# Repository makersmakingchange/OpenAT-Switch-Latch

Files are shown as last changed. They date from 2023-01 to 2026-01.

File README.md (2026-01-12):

<!--- Open Source Assistive Technology: GitHub Readme Template Version 1.2 (2024-May-27)  --->

<!--- TITLE --->
# OpenAT Switch Latch 
The OpenAT Switch Latch is a switch adapter that enables a standard momentary assistive switch to be used as a toggle switch or latch. Activating and releasing the input switch will turn on and hold on the output. Activating and releasing the input switch again will turn the connected output device off. The device requires one CR2032 coin cell battery for operation. 

This device was developed as several assistive switch users requested the ability to control lights and other devices in a semi-permanent manner utilizing their preferred momentary assistive switches.

The OpenAT Switch Latch is comprised of off-the-shelf electronics, a custom printed circuit board (PCB) and 3D printed parts.

The OpenAT Switch Latch is open assistive technology (OpenAT). Under the terms of the open source licenses, the device may be built, used, and improved upon by anyone.

The overall cost of materials for a single build is approximately $67 CAD. The cost of materials when built in quantity is $38 CAD.

> [!IMPORTANT]
2025-Nov-06: One of the electronic components in this design has been discontinued (MOSFET IRLD014PBF) and is no longer available on DigiKey or Mouser. In the short term, there are some alternative sources (e.g., https://www.amazon.ca/10PCS-IRLD110-DIP4-IRLD110PBF-DIP-4/dp/B0DSSJTPH8). In the longer term, we are working on updating the design with an alternative component.  

Last updated: 2026-Jan-12

## Usage
To setup the OpenAT Switch Latch, a momentary switch is plugged into the 3.5 mm jack marked 'Input' and the device to be controlled is plugged into the 3.5 mm jack marked 'Output'.

To use the device it must be powered on by sliding the Power Switch towards the left to the On position. When the assistive switch is activated, the LED indicator light will turn on and remain on, and the output device will be activated. When the assistive switch is activated again, the LED indicitor light will turn off and remain off, and the output device will be deactivated.

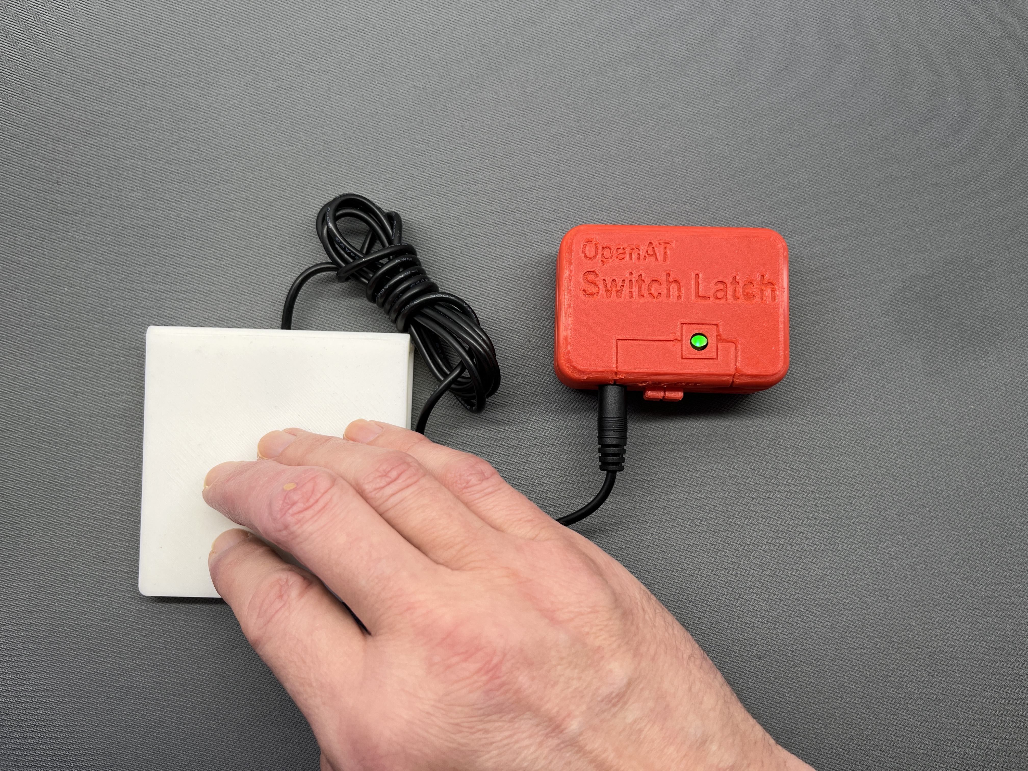
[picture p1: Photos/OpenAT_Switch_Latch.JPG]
An OpenAT Switch Latch pictured with a person pressing an input switch.


## More info at
- [Makers Making Change Library Page](https://www.makersmakingchange.com/s/product/switch-latch/01tJR00000095zlYAA)

## How to Obtain a OpenAT-Switch-Latch
### 1. Do it Yourself (DIY) or Do it Together (DIT)

This is an open-source assistive technology, so anyone is free to build it. All of the files and instructions required to build the OpenAT-Switch-Latch are contained within this repository. Refer to the Maker Checklist below.

### 2. Request a build of this device

If you would like to obtain a OpenAT Switch Latch, you may submit a build request through the [MMC Library Page](https://www.makersmakingchange.com/s/product/switch-latch/01tJR00000095zlYAA). The requestor is responsible for the cost of materials and any shipping.

### 3. How to build this device for someone else

If you have the skills and equipment to build this device, and would like to donate your time to create the switch for someone who needs it, visit the [MMC Maker Wanted](https://makersmakingchange.com/maker-wanted/) section.

## Getting Started

### 1. Read the Makers Checklist

The [Makers Checklist](/Documentation/OpenAT_Switch_Latch_Maker_Checklist.pdf) provides an overview of the steps required to build this device.

### 2. Order the Off-The-Shelf Components

The [Bill of Materials](/Documentation/OpenAT_Switch_Latch_BOM.csv) lists all of the parts and components required to build the OpenAT-Switch-Latch. The main switch component needs to be ordered online. The rest of the off-the-shelf components are also online or may be available in smaller quantities at your local hardware store or dollar store.

### 3. Order the PCBs

The [Gerber_Files](/Build_Files/PCB_Build_Files/Gerber_Files) includes the PCB build information which can be submitted to PCB fabrication service to create the custom PCB. Please refer to MMC-PCB for more information on custom PCB fabrication.

### 4. Print the 3D Printable components

All of the files and individual print files can be in the [/Build_Files/3D_Printing_Files](/Build_Files/3D_Printing_Files/) folder.

### 5. Assemble the OpenAT-Switch-Latch

Reference the [Assembly Guide](/Documentation/OpenAT_Switch_Latch_Assembly_Guide.pdf) for the tools and steps required to build each portion.

## Files

### Documentation
| Document             | Version | Link |
|----------------------|---------|------|
| Design Rationale     | 1.0     | [OpenAT_Switch_Latch_Design_Rationale](/Documentation/OpenAT_Switch_Latch_Design_Rationale.pdf)     |
| Maker Checklist      | 1.0     | [OpenAT_Switch_Latch_Maker_Checklist](/Documentation/OpenAT_Switch_Latch_Maker_Checklist.pdf)     |
| Bill of Materials    | 1.2.1    | [OpenAT_Switch_Latch_Bill_of_Materials](/Documentation/OpenAT_Switch_Latch_BOM.csv)     |
| 3D Printing Guide    | 1.0     | [OpenAT_Switch_Latch_3D_Printing_Guide](/Documentation/OpenAT_Switch_Latch_3D_Printing_Guide.pdf)     |
| Assembly Guide       | 1.2.1     | [OpenAT_Switch_Latch_Assembly_Guide](/Documentation/OpenAT_Switch_Latch_Assembly_Guide.pdf)     |
| User Guide           | 1.0     | [OpenAT_Switch_Latch_User_Guide](/Documentation/OpenAT_Switch_Latch_User_Guide.pdf)    |

### Design Files

 - [CAD Design Files](/Design_Files/CAD_Design_Files)
 - [PCB Design Files](/Design_Files/PCB_Design_Files)

### Build Files

 - [3D Printing Files](/Build_Files/3D_Printing_Files)
 - [PCB Build Files](/Build_Files/PCB_Build_Files)

## License
Copyright (c) 2023-2024 Neil Squire Society.

This repository describes Open Hardware:
 - Everything needed or used to design, make, test, or prepare the OpenAT Switch Latch is licensed under the [CERN 2.0 Weakly Reciprocal license (CERN-OHL-W v2) or later](https://cern.ch/cern-ohl ) .
  - Accompanying material such as instruction manuals, videos, and other copyrightable works that are useful but not necessary to design, make, test, or prepare the Forest Hub are published under a [Creative Commons Attribution-ShareAlike 4.0 license (CC BY-SA 4.0)](https://creativecommons.org/licenses/by-sa/4.0/) .

You may redistribute and modify this documentation and make products using it under the terms of the [CERN-OHL-W v2](https://cern.ch/cern-ohl).
This documentation is distributed WITHOUT ANY EXPRESS OR IMPLIED WARRANTY, INCLUDING OF MERCHANTABILITY, SATISFACTORY QUALITY AND FITNESS FOR A PARTICULAR PURPOSE.
Please see the CERN-OHL-W v2 for applicable conditions.

Source Location: https://github.com/makersmakingchange/OpenAT-Switch-Latch

## Contributors
 
 - Derrick Andrews, Neil Squire Society. Concept generation, circuit design, testing, documentation.
 - Milad Hajihassan, Neil Squire Society. PCB Layout.
 - Jake Mclvor, Neil Squire Society. Enclosure design, documentation. 

---

<!-- ABOUT MMC START -->
## About Makers Making Change
[Makers Making Change Logo](https://www.makersmakingchange.com/)

Makers Making Change is a program of [Neil Squire](https://www.neilsquire.ca/), a Canadian non-profit that uses technology, knowledge, and passion to empower people with disabilities.

Makers Making Change leverages the capacity of community based Makers, Disability Professionals and Volunteers to develop and deliver affordable Open Source Assistive Technologies.

 - Website: [www.MakersMakingChange.com](https://www.makersmakingchange.com/)
 - GitHub: [makersmakingchange](https://github.com/makersmakingchange)
 - Bluesky: [@makersmakingchange.bsky.social](https://bsky.app/profile/makersmakingchange.bsky.social)
 - Instagram: [@makersmakingchange](https://www.instagram.com/makersmakingchange)
 - Facebook: [makersmakechange](https://www.facebook.com/makersmakechange)
 - LinkedIn: [Neil Squire Society](https://www.linkedin.com/company/neil-squire-society/)
 - Thingiverse: [makersmakingchange](https://www.thingiverse.com/makersmakingchange/about)
 - Printables: [MakersMakingChange](https://www.printables.com/@MakersMakingChange)

### Contact Us
For technical questions, to get involved, or to share your experience we encourage you to [visit our website](https://www.makersmakingchange.com/) or [contact us](https://www.makersmakingchange.com/s/contact).
<!-- ABOUT MMC END -->

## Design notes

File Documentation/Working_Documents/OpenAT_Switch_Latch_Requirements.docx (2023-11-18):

### 1.1.1 Introduction

Many assistive switches are the momentary type; however, it is often desirable to use such switches in a toggle switch manner to allow long duration use of a switched device.

# 1. Problem Definition

## 1.1 Who

Who will be using the device?

- Users who are unable (or prefer not) to activate an assistive switch for extended time periods.

Who will be affected by the device?

- Users who wish to control lights and other devices in a semi permanent manner, by utilizing their preferred momentary assistive switches.

## 1.2 What

What must the device do?

- Set a toggle switch output to it’s opposite state, whenever the assistive switch is connected to the input, and enabled.

What needs must the device serve?

- Ability to control lights, tools, music effects, or toys for long durations.

## 1.3 Why

Why will the device be used?

- Because existing assistive switches are usually momentary, and toggleable switches are unlikely to be found in many assistive switch classes.

## 1.4 Where

- In homes, offices, or other work environments.

## 1.5 When

- When a device needs to be enabled for more than a few seconds.

# 2. Functional Properties

## 2.1 Goals

ID | Description
G01 | Cost-effective
G02 | Optimized for low-volume builds (I.e., 1)
G03 | Open-Source Hardware
G04 | Enable a momentary assistive switch to toggle (latch) a switch controllable device.
G05 | Minimize material cost
G06 | Sustainability

## 2.2 Functional Requirements

ID | Description
F01 | The device shall have one or more input channels.
F02 | Long duration operation (many days of operation on battery power).
F03 | The device should have a visual feedback element to indicate switch activation ( Example: LED)
F04 | The device should allow activation by plugging a cable into the input jack and should default to a non-closed connection.
F05 | The OpenAT Switch Latch should have a power switch to reduce power consumption when not being used.
F06 | The battery hatch should provide a screw to prevent children from swallowing the lid or the battery underneath.
F07 | The device should have a capacitor for input circuit switch input debouncing, as the device will not be able to achieve this using software.
F08 | When off, the circuit must activate (and stay active) when a switch input is triggered.
F09 | When on, the circuit must de-activate (and stay off) when a switch input is triggered.
F10 | The circuit must contain some form of switch debouncing circuitry to keep operation reliable.

## 2.3 Non-functional Requirement

ID | Description
NF01 | Shall look professional with tight tolerance on case size.
NF02 | Input ports should be legibly labelled for easy identification
NF03 | The device should require no mechanical force to operate.
NF04 | The device should have a long battery life.
NF05 | The toggle Adapter should use a minimum of electronic parts.

## 2.4 Constraints

ID | Description
C01 | The OpenAT Switch Latch must be able to be constructed using basic ‘maker’ tools.
C02 | The OpenAT Switch Latch should be able to be disinfected using detergent and alcohol.

© 2023 by Neil Squire / Makers Making Change. This work is licensed under the CC BY SA 4.0 License: http://creativecommons.org/licenses/by-sa/4.0 Files available at https://makersmakingchange.com/project/OpenAT-Switch-Latch/ Page 1 of 1

V1.0 | January 2023 OpenAT-Switch-Latch requirements Specifications

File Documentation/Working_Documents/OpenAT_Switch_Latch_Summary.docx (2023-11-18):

# Title

## OpenAT Switch Latch

## Subtitle

A switch adapter that allows a momentary assistive switch to act as a toggle switch.

## Device Specifications

Build Time:

< 1hr

Cost:

$50-$100

Stage: Recently Added

Skills:

Need: Electronics, Soldering, 3D Printing, Custom PCB, Engineering

Disability: Mobility / Physical, Cognitive / Learning

Difficulty: Intermediate

License: Attribution-ShareAlike 4.0 International

Usages: Aids for Daily Living, Environmental Control, Recreation and Leisure, Computer Access

Type:

Designer: Makers Making Change

## Device Details

### Overview

### The OpenAT Switch Latch converts a momentary switch input into a toggle switch output. The device was developed as several assistive switch users requested the ability to control lights and other devices in a semi-permanent manner, but do so, utilizing their preferred momentary assistive switches.

### The intended users of the OpenAT Switch Latch are those who require a momentary switch to act as a toggle switch (e.g., latched switch), allowing the user to turn on for an extended time with a quick tap, and off again with another quick tap.

### Usage

### To setup the Open AT Switch Latch adapter, a momentary switch is plugged into the 3.5 mm jack marked 'Input' and the device to be controlled is plugged into the 3.5 mm jack marked 'Output'.

To use the device it must be powered on by sliding the Power Switch towards the left to the On position. When the assistive switch is activated, the LED indicator light will turn on and remain on, and the output device will be activated. When the assistive switch is activated again, the LED indicator light will turn off and remain off, and the output device will be deactivated.

### Cost

~$50.54 ($20.54 Components and 3D prints; ~$30 for 5 custom PCBs)

### Build Instructions

The OpenAT Switch Latch consists of 3D printed parts, a custom PCB, and electronic components. All documentation including an Assembly Guide is available at the GitHub repository.

#### Skills Required

- 3D Printing
- Soldering
- Custom PCB

#### Time Required

- 3D Printing Time: 2 Hours and 40 Minutes
- Assembly Time: 1 Hour

#### Tools

- Soldering Iron and 60/40 electronics solder
- Needle nose pliers
- Side cutters
- Medium Phillips screwdriver

#### Components

1. 1X 470K Resistor
2. 1X 22K Resistor
3. 1X Texas Instruments CD74HC73E Flip-Flop
4. 1X 1uF Capacitor
5. 1X #4-3/6" Pan Head Screw
6. 1X OpenAT-Switch-Latch PCB (Printed Circuit Board)
7. 1X CR2032 Battery holder
8. 2X IRLD-110 MOSFET
9. 1X 10K Resistor
10. 1X 0.1uF Capacitor
11. 2X SJ-3566AN 3.5mm Audio Stereo Jack
12. 1X Slide Switch
13. 1X LED (green, super bright)
14. 4X #4-3/8" Pan Head Screw
15. 1 X CR2032 Battery

#### 3D Printing

1. 1X 3D Printed Enclosure Top
2. 1X 3D Printed Enclosure Bottom
3. 1X 3D Printed LED Spacer
4. 1X 3D Printed Switch Slide
5. 1X 3D Printed Battery Cover

#### Custom PCB

This design utilizes a custom PCB. Five boards (minimum quantity) can be obtained for approximately $30 CAD (shipping included).

### Design

The PCB was designed using Autodesk EAGLE, and the enclosure was designed using Autodesk Fusion 360.

### Attribution

Designed by Makers Making Change

- Circuit design by Derrick Andrews, Makers Making Change
- PCB Layout by Milad Hajihassan, Makers Making Change
- Enclosure design by Jake Mclvor, Makers Making Change

© 2023 by Neil Squire / Makers Making Change. This work is licensed under the CC BY SA 4.0 License: http://creativecommons.org/licenses/by-sa/4.0 Files available at https://makersmakingchange.com/project/OpenAT-Switch-Latch/ Page 1 of 2

V1.0 | December 2022 OpenAT Switch Latch Summary

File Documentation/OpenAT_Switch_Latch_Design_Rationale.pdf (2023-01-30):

V1.0 | Aug 2022

## OpenAT Switch Latch

## DESIGN RATIONALE

© 2023 by Neil Squire / Makers Making Change. This work is licensed under the CC BY SA 4.0 License: http://creativecommons.org/licenses/by-sa/4.0 Files available at https://makersmakingchange.com/project/OpenAT-Switch-Latch/

### Introduction

The OpenAT Switch Latch was developed when a number of assistive switch users (Ean Price, Tom Cretain) requested the ability to control lights and other devices in a semi permanent manner, but do so, utilizing their preferred momentary assistive switches.

The intended users of the OpenAT Switch Latch are those who require a momentary switch to act as a toggle switch (aka latched switch), allowing the user to turn on for an extended time with a quick tap, and off again with another quick tap.

### Research

### Commercial Options

AbleNet Dual Switch Latch & Timer

The Dual Switch Latch & Timer by Adaptive Tech Solution $305.22

Switch Latch & Timer (adaptivetechsolutions.com) (https://www.adaptivetechsolutions.com/dual-switch-latch-timer/)

Most switches give switch users momentary control of their switch adapted toys or appliances. Meaning, when you press your switch, your toy or appliance will operate only for the time that you are holding down the switch. The Dual Switch Latch and Timer gives switch users more control of their devices by adding time and latch modes of control. You can setup two switches into the Switch Latch and timer. The switches will operate their corresponding toy or appliance independently of each other in the same mode of control.

Switch Capable Continuous Control Unit

## DESIGN RATIONALE

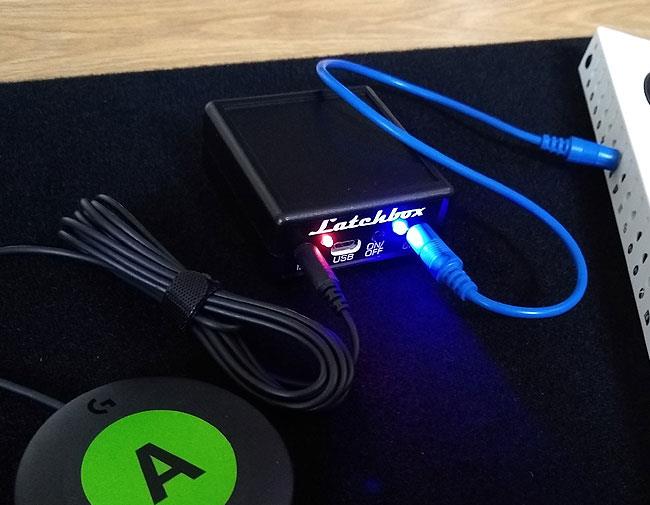
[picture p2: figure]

© 2023 by Neil Squire / Makers Making Change.

can be used to operate most AC appliances from up to 20 feet away. List Price: $315.40 Sale
Price: $220.56 (Save 30%)

The Switch Capable Continuous Control Unit can be used to operate most AC appliances from up to 20 feet away. Activate the remote transmitter with a capability switch after plugging the appliance into the receiver. In latch mode, the appliance will run until the switch is pressed again; in momentary mode, it will turn on when the switch is pressed and off as soon as the switch is released.

PowerLink 4
https://www.ablenetinc.com/powerlink-4-north-america/

Cost: $330 USD + Shipping

Used to turn on appliances that are powered from a wall outlet.

Latch Box
Link: https://oneswitch.org.uk/art.php?id=276

Cost: £40 (+ postage) (~$62 CAD + shipping)

Power: 3x AAA batteries OR USB (Micro-B)

## DESIGN RATIONALE

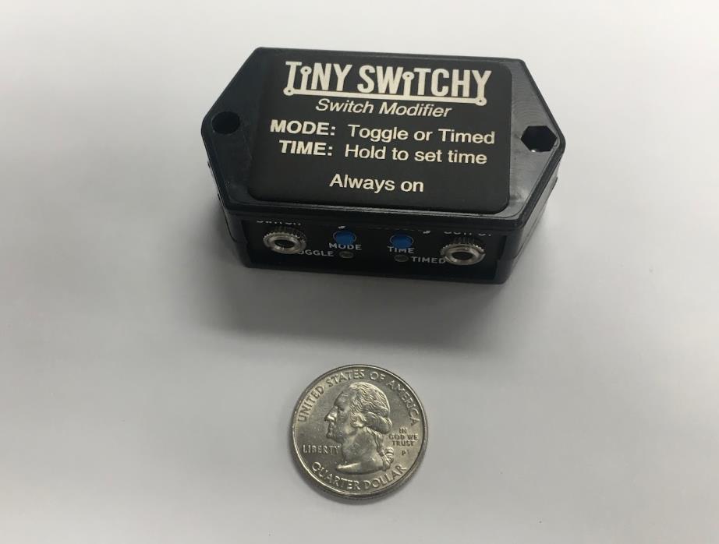
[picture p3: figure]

© 2023 by Neil Squire / Makers Making Change.

Tiny Switchy Version 1.4

Information: https://www.tinyswitchy.com/

Purchase: https://www.littlelaketech.com/product/tiny-switchy/1#

Cost: $40 USD + Shipping. Does not currently ship to Canada.

- Toggle and timed-output modes
- 3V CR2032 Coin cell battery
- Expected battery life: 3 years
- Small
- >1 A switched current
- Maximum hold time: 68 minutes

### DIY Versions

Self-Retention for Button on Xbox Adaptive Controller
Link: http://www.johannes-online.de/wordpress/?page_id=1063
- Based on request from Melly (https://meilert.net/) (https://twitter.com/melly_maeh)
- LED to indicate status

## DESIGN RATIONALE

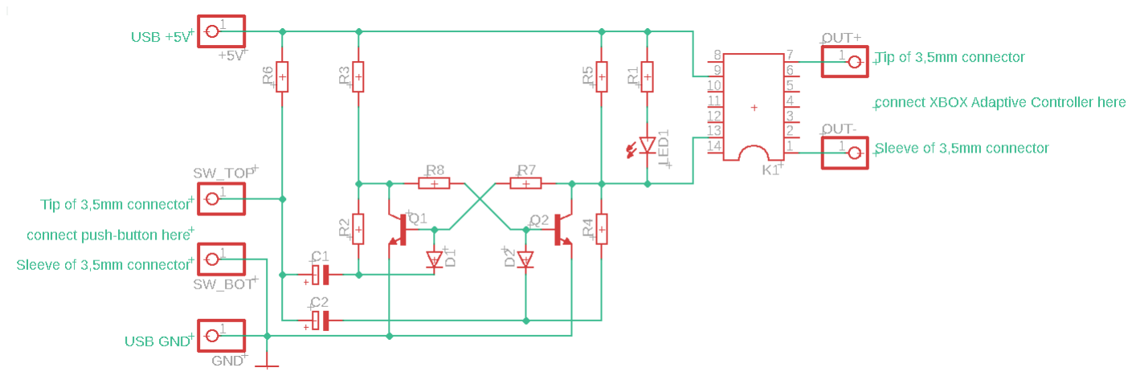
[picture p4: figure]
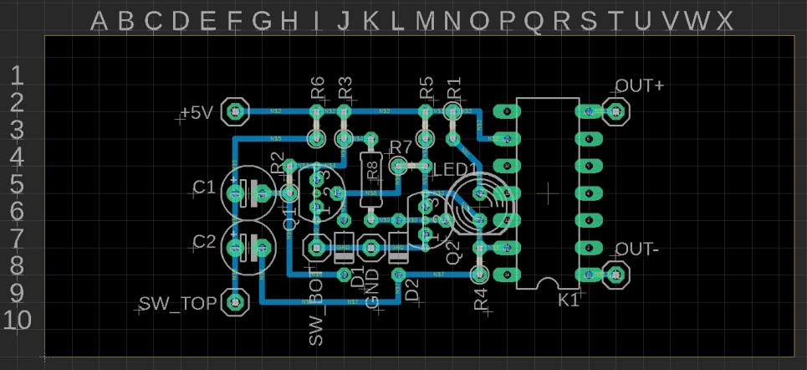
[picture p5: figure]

© 2023 by Neil Squire / Makers Making Change.

Position | Designation | Number
C1, C2 | Electrolytic capacitor 22 μF | 2
D1, D2 | Diode 1N4007 | 2
K1 | Reed Relay V23100-V4005-A010 | 1
LED1 | LED 5mm, red | 1
Q1, Q2 | Transistor BC547 | 2
R1, R2, R3, R4, R5 | Resistor 1k Ohm | 5
R6, R7, R8 | Resistance 10k Ohm | 3

30 mm x 70 mm Grid board

## DESIGN RATIONALE

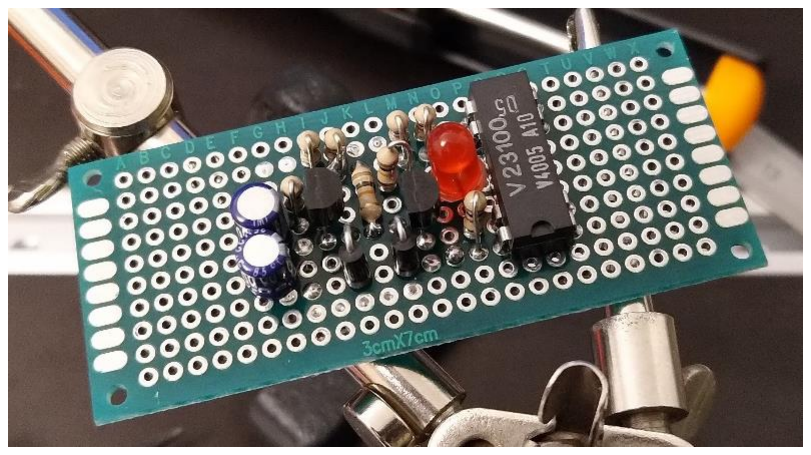
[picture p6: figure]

© 2023 by Neil Squire / Makers Making Change.

https://youtu.be/RP3qliKeLuE

https://youtu.be/2iWaojsw_O0

### Requirements

### Goals

G01 | Enable a momentary assistive switch to toggle (latch) a switch controllable device.
G02 | To make the device with a relay output capable of driving powered devices.
G03 | To make the unit accept 3.5 mm assistive switches.
G04 | Battery life of XX

### Functional Requirements

F01 | When off, the toggle circuit must activate (and stay active) when a switch input is triggered.
F02 | When on, the toggle circuit must de-activate (and stay off) when a switch input is triggered.
F03 | The toggle circuit must contain some form of switch debouncing circuitry to keep operation reliable.
F04 | The toggle circuit should default to a non-closed connection.

### Non-functional Requirement

NF01 | The Toggle Adapter should require no mechanical force to operate.
NF02 | The toggle Adapter should have a long battery life.

## DESIGN RATIONALE

© 2023 by Neil Squire / Makers Making Change.

NF03 The toggle Adapter should use a minimum of electronic parts.

### Constraints

C01 | The MMC Toggle Adapter must be able to be constructed using basic ‘maker’ tools.
C02 | The MMC Toggle Adapter should be able to be disinfected using detergent and alcohol.

## DESIGN RATIONALE

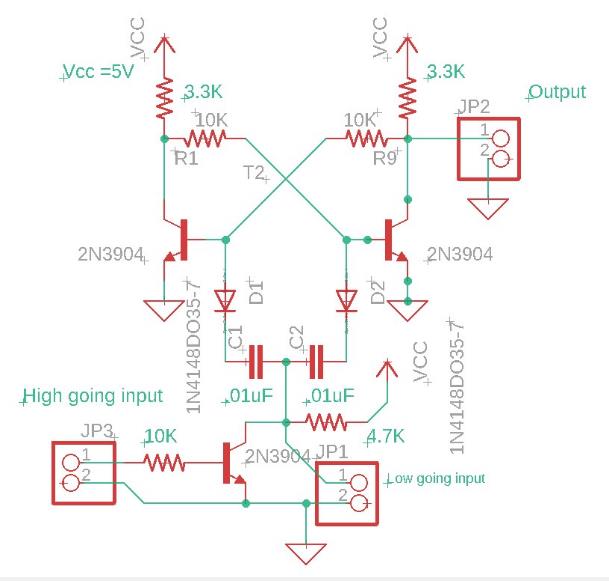
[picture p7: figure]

© 2023 by Neil Squire / Makers Making Change.

### Ideation

Some electronic toggle circuit diagrams were sourced from the internet as potential candidates for forming the core of the MMC Toggle Adapter. The ideal candidate circuit will have inexpensive parts that are small in number and are easy to construct with basic hand tools.

### Conceptual Design

### Toggle Circuit Options

Concept 1: Two Transistor Flip-Flop

Two Transistor Flip Flop circuit

This circuit comprises of just two low cost and extremely available transistor and a reasonable number of resistors and capacitors. As no microchip is required, many electronics engineers and hobbyists will find they already posses the needed garden variety parts. The main downsides are that more parts are needed, and that the power consumption of this concept is highest.

## DESIGN RATIONALE

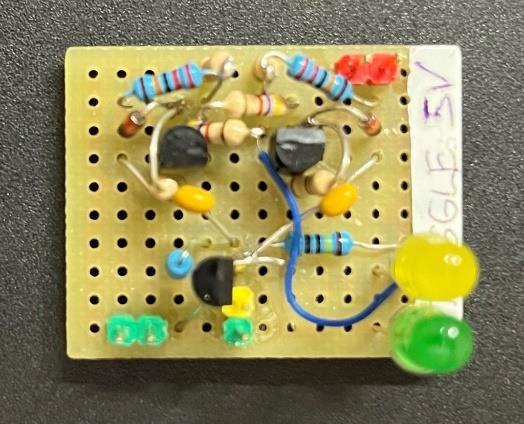
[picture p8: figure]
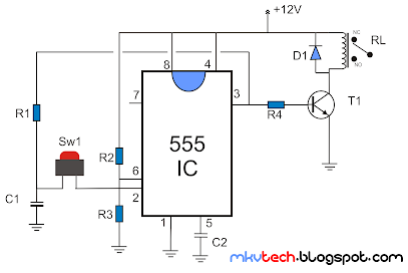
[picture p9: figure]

© 2023 by Neil Squire / Makers Making Change.

Concept 1 prototype was built on Perfboard using parts already in stock. As the parts count is quite high having a PCB design would be best for the final version The diode steering works reliably, as the discrete bipolar transistors have a higher noise immunity than CMOS type input circuitry. The downside comes in the form of higher power consumption, which can be a problem if using batteries.

Concept 2: 555 Timer IC

555 Timer IC

The venerable 555 Timer IC is used for the second concept. Note that the lower power CMOS version is used here. The chip is easy to solder as it only has eight pins. Power consumption is about 80 micro amps, the second lowest.

## DESIGN RATIONALE

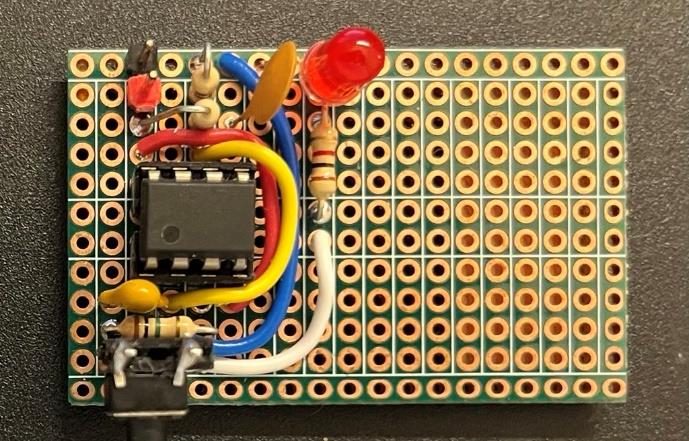
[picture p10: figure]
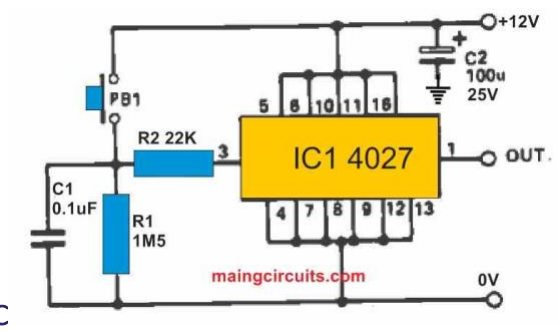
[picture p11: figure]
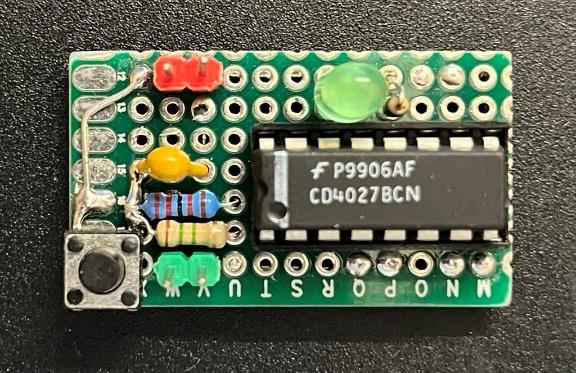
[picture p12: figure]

© 2023 by Neil Squire / Makers Making Change.

The concept 2 prototype was built on double sided Perfboard using parts ordered from Digi-Key. Note that this circuit makes use of the CMOS version of the 555 timer IC, which is considerably more energy efficient than the original (but still available) bipolar version. Putting this one together was noticeably easier, as the total part count is nearly half that of the discrete transistor version.

Concept 3: Dual Flip Flop IC
The low power CMOS CD4027BCN Dual Flip Flop IC is used here. While the IC has 16 pins to solder, they can all be soldered quickly because all pins go into a PCB together, and can be soldered quickly due to being placed in rows. Note that this chip has the lowest power consumption of the concepts presented here. Current draw is a mere .7 micro amps, so this circuit could run on a coin cell for months.

Concept 3 prototype was built on double sided Perfboard using parts ordered from Digi-Key. The low power CMOS CD4027BCN Dual Flip Flop IC is used here. While the IC has 16 pins to solder, they can all

## DESIGN RATIONALE

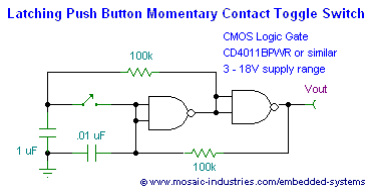
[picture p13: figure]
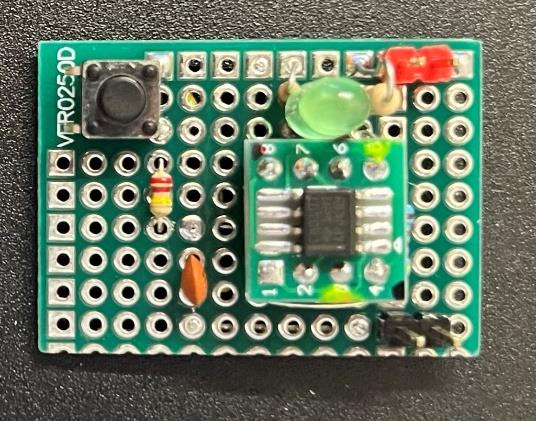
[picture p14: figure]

© 2023 by Neil Squire / Makers Making Change.

be soldered quickly as they are in rows, and all go in together. Note that this chip has the lowest power consumption of the concepts presented here. Current draw is a mere .7 micro amps, so this circuit could run on a coin cell for months. An additional bonus of this design is that this IC can be used to make two toggle switches without having to buy another chip. It just requires an extra three resistors, and a capacitor of the same values.

Concept 4: Quad NAND Gate IC CD40107BM96 dual NAND gate

Concept 3 prototype was built on double sided Perfboard using parts ordered from Digi-Key. The low power CMOS CD4027BCN Dual Flip Flop IC is used here. ng, so the design was changed to incorporate a bearing instead.

## DESIGN RATIONALE

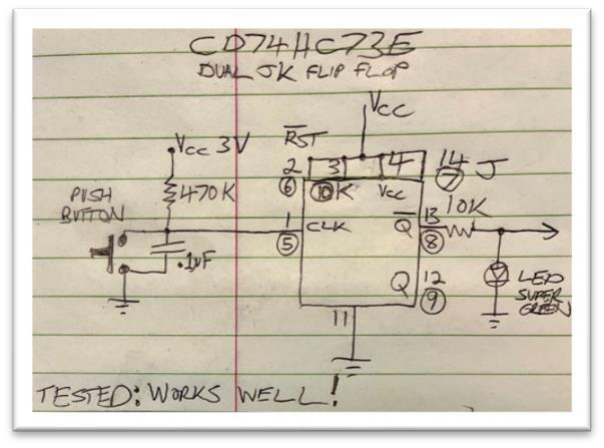
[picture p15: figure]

© 2023 by Neil Squire / Makers Making Change.

Concept 5 Flip Flop with buffered inputs
The CD74HC73E was chosen when it was determined that the input circuitry of the flip flop was vital to the behaviour of the latching circuit when fed with a mechanical switch instead of normally expected CMOS or TTL level circuitry. It was found, that despite identical part numbers, parts from different manufacturers had different input structures suitable for switch inputs. We liked the CD74HC73E because it had an input buffer that could condition a rougher input signal into a usable form, without having to add extra circuitry. Additionally, this chip drew remarkably little power, while still being able to provide decent output drive.

Component List:

### Circuit Comparison

| Concept 1 Discrete transistor Flip-Flop | Concept 2 555 Timer IC | Concept 3 CD4027 Flip-Flop IC | Concept 4 Quad NAND gate IC | Concept 5 TI CD74HC73E Dual Flip Flop
Current Draw (all at 3.3V) | 959 uA (2.37 mA + LED) | 88-90 uA (1.35+LED) | .2 uA (86.2 uA+LED) | 4.9 uA | .4uA 67uA with LED on
Noise Immunity | Excellent | Poor: pin 2 input of 555 highly susceptible to | Acceptable: .85 VAC RMS | Fail Circuit fails to change states when | Excellent

## DESIGN RATIONALE

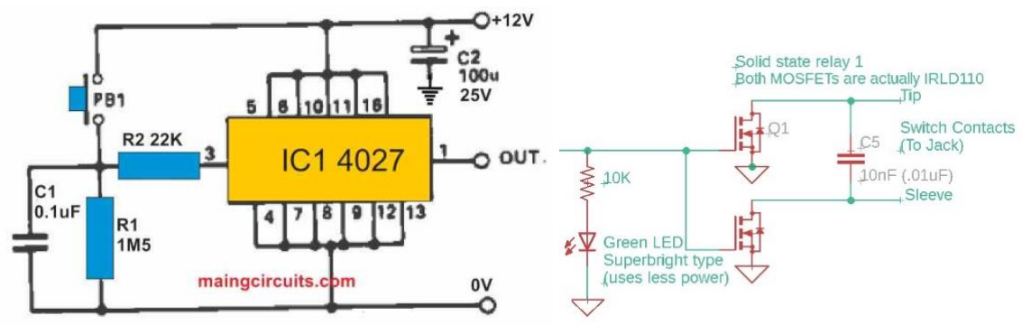
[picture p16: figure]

© 2023 by Neil Squire / Makers Making Change.

| withstood 1.7 VAC RMS) on input | noise .25 VAC RMS | | wires are added. | Works even with longer cables
Price | Under $20 for core circuitry | Under $20 for core circuitry | Under $20 for core circuitry | Under $20 for core circuitry | Under $20 for core circuitry
Projected ease of build | Moderate | Very Easy | Easy | Easy | Easy

### Toggle Circuit

As the leading design from the comparison table is using the CD4027 IC, we will focus on the CD4027. Note that all the test circuits omitted a solid state relay output circuit, which we will add to the final design, and will become sum of the two schematics below:

## DESIGN RATIONALE

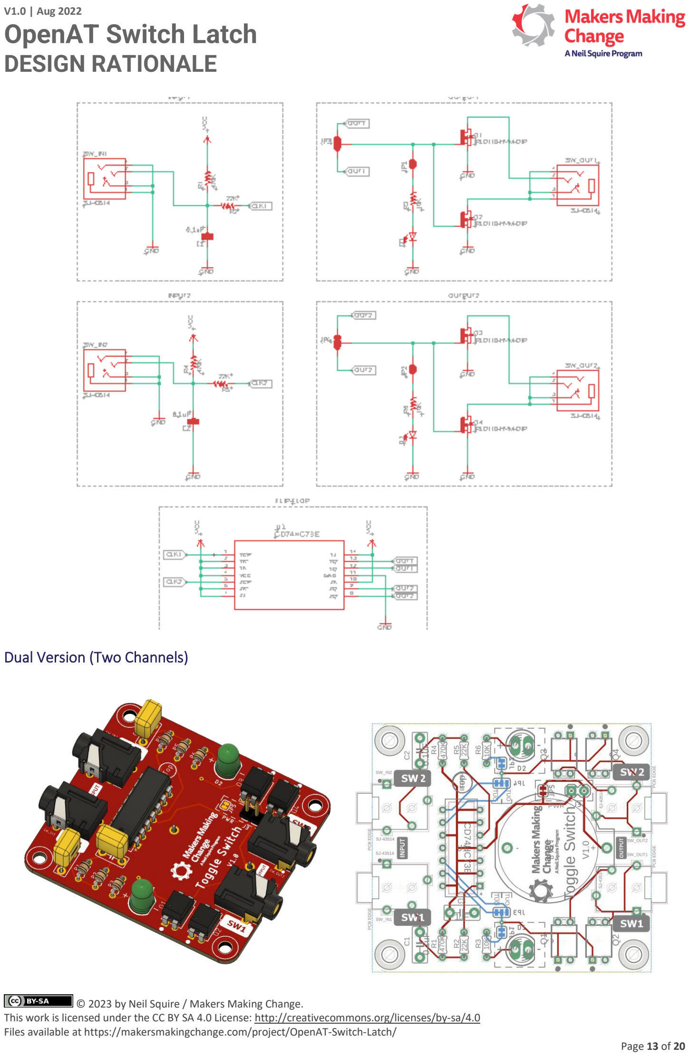
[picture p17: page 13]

© 2023 by Neil Squire / Makers Making Change.

Dual Version (Two Channels)

## DESIGN RATIONALE

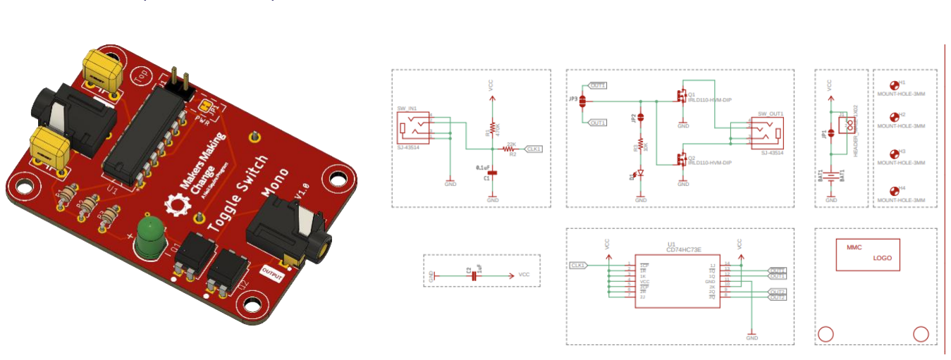
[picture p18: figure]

© 2023 by Neil Squire / Makers Making Change.

Dual Construction Method Comparison
| PCB | PCB-A Thru-hole | PCB-A SMD | Protoboard
Number of components | 22 | N/A | N/A | N/A
Number of polarized components | 7 | N/A | N/A | N/A
Number of connections | 72 | N/A | N/A | N/A
Cost | $28 CAD | N/A | N/A | N/A
Size | 56mm x 50mm | N/A | N/A | N/A
Maker Difficulty | Medium | Medium | High | High

Mono Version 1 (One Channel)

## DESIGN RATIONALE

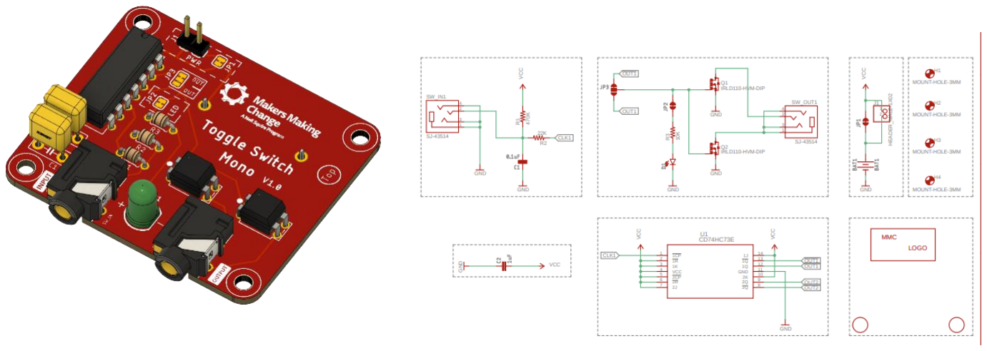
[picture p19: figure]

© 2023 by Neil Squire / Makers Making Change.

Mono Version 2 (One Channel)

Mono Construction Method Comparison
| PCB | PCB-A Thru-hole | PCB-A SMD | Protoboard
Number of components | 12 | N/A | N/A | N/A
Number of polarized components | 4 | N/A | N/A | N/A
Number of connections | 46 | N/A | N/A | Additional jumpers needed on protoboards
Cost | $20 CAD | N/A | N/A | N/A
Size | 56mm x 38mm or 52mm x 44mm | N/A | N/A | Additional area may be needed
Maker Difficulty | Easy | Moderate | SMD soldering skills needed | Recommend Experienced builders only

## DESIGN RATIONALE

© 2023 by Neil Squire / Makers Making Change.

### Power Source

AAA Cells
Pros
- Rechargeable

Cons

- Can leak over long time durations

Lithum 3V Cells
Pros
- High energy density, unlikely to leak.

Cons

- Potential fire risk for some brands/formulations

Comparison

AAA cells are more readily available in stores, but 3V lithium batteries are less common, though CR2032 coin cells are reasonably common.

### Layout

### Visual Feedback

(Nothing)

LED
High brightness (efficient) green LED used with higher value resistor for lower current draw.

### Test Button

No test button is chosen.

### Power Switch

Internal jack switch

## DESIGN RATIONALE

© 2023 by Neil Squire / Makers Making Change.

External slide switch

### Detailed Design

### OpenAT Switch Latch V1.0

Channels
This design uses a single channel.

Visual Feedback
This design has a single green LED. When the output is closed, the LED is on. When the output is open, the LED is off. There is a cuttable junction for disabling this feature.

Power Source
3V Lithium CR2032 Cell in a thru-hole mounted holder.

Power Switch
This design has a sliding power switch.

Enclosure
This design has a multipart 3D printed enclosure fastened with screws. The enclosure consists of a top, bottom, battery cover, and switch slide. The PCB is affixed inside to the top portion of the enclosure. The bottom of the enclosure is affixed to the top of the enclosure using four (4) screws. The battery cover is held in with a single screw.

## DESIGN RATIONALE

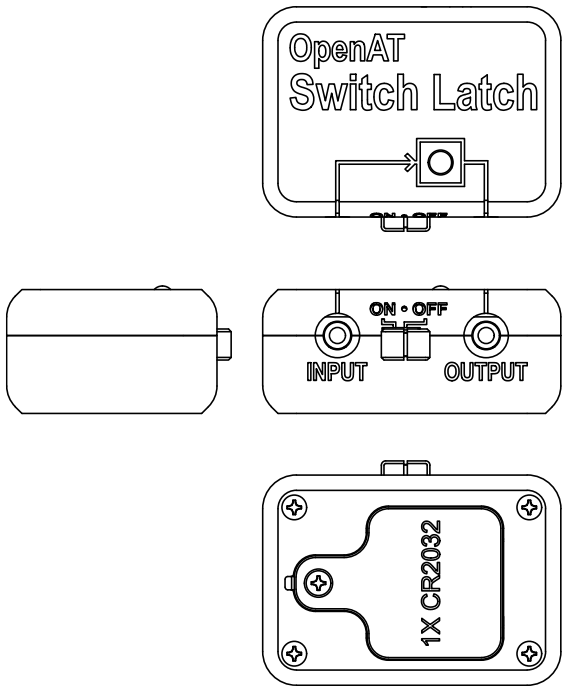
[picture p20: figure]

© 2023 by Neil Squire / Makers Making Change.

Layout

Design Changes
- Add footprint for right angle switch with a cut-able bypass junction (switch on by default)
- Add Jack with built in switch to act power switch and mark switch pins on PCB (to allow for bypass in case of failure I.e. Digi-Key SJ-3566AN or equivalent)
- Add Clearance around the PCB and battery holder (2.5-3 mm?)
- Add central hole on PCB same size as 4 corner holes.
- Change Dimensions of PCB to 60 x 40 mm
- Move alternate output cut-able trace to under battery case (allows for testing but not final use)
- Move input and output jacks apart as much as possible (but allow 1mm clearance to case posts)
- Move the power switch between input and output jacks
- Move LED to right of switch
- Change the JK flip flop IC to Texas Instruments CD74HC73E, as CD4027 from Fairchild was no longer available from Digi-Key or Mouser, and the newer revisions from other vendors had gate

## DESIGN RATIONALE

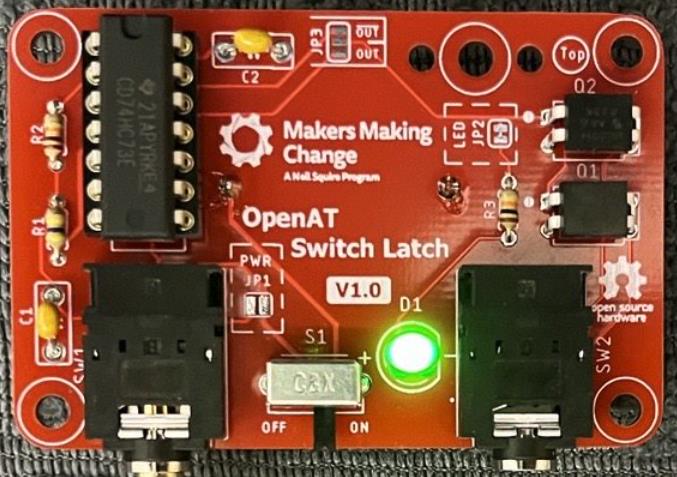
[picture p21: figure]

© 2023 by Neil Squire / Makers Making Change.

input structures that proved unsuitable for use with a mechanical switch input, as this type of circuit is normally fed with pulses from another logic IC

### Opportunities for Improvement

- Modify design with extra capacitor (or diode) to boost the noise immunity somewhat.
- Use non polarized ceramic capacitor for power decoupling.
- Modify circuit to become a dual toggle switch, as only six extra parts are required.
•

Printed Circuit Board

Theory of Operation

- Pressing the button causes the input of the first JK Flip Flop to go low. This triggers the Flip Flop output to change to its opposite state, and remaining that way (even after the button is released, and the input goes high again). Only a fresh button press will change the output state. The output of the Flip Flop feeds a green LED for state indication, via a 10K resistor. The Flip Flop output is also connected to two MOSFETs, which are wired together to function as a solid state relay. Thus, when the Flip Flop output goes high, and the LED turns on, the output jack also becomes conductive, turning on any connected and activatable device.

## DESIGN RATIONALE

© 2023 by Neil Squire / Makers Making Change.

JP1

- Default: Unsoldered
- Purpose: This can be soldered to bypass the input jack switch (i.e., the device’s power is controlled only by the power switch)

JP2

- Default: Soldered
- Purpose: This can be cut to disable the Output LED.

JP3

- Default: Reverse toggle switch operation

Final PCB Changes

- Change name
- Move JP3 to be accessible when device is constructed.

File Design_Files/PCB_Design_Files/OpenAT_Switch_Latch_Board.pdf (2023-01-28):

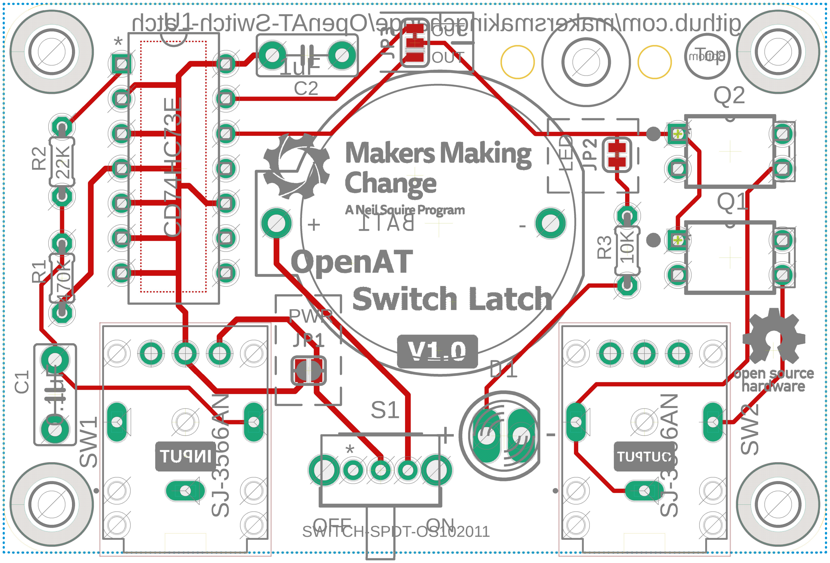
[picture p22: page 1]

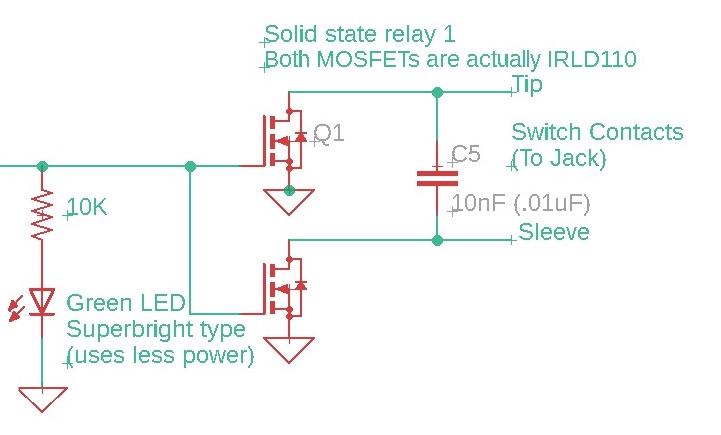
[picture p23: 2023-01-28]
Documentation/Working_Documents/Photos/Solid State relay schematic.jpg

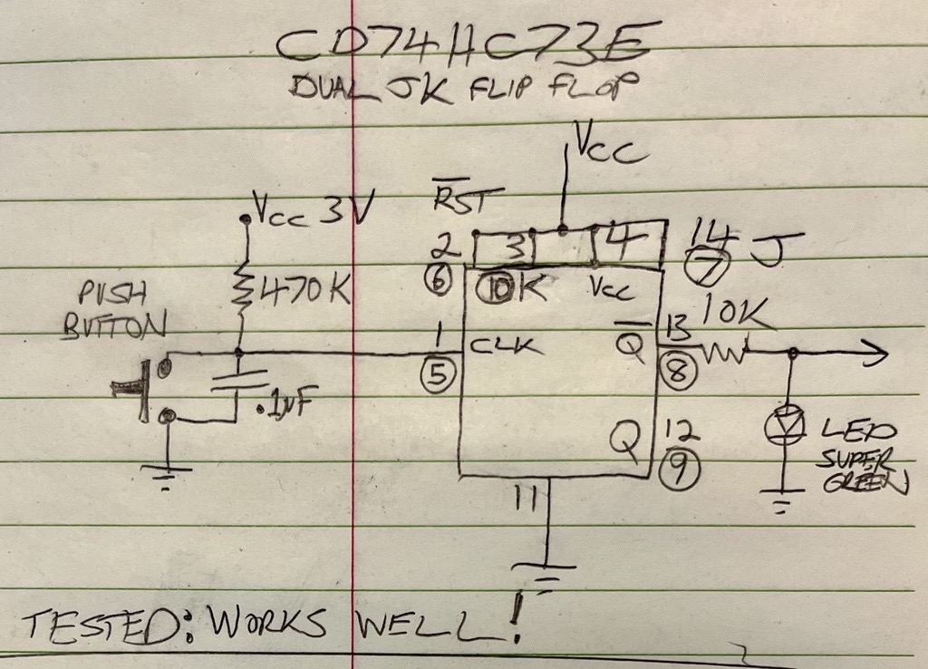
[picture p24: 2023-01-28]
Documentation/Working_Documents/Photos/Switch_Latch_SchematicSketch.png

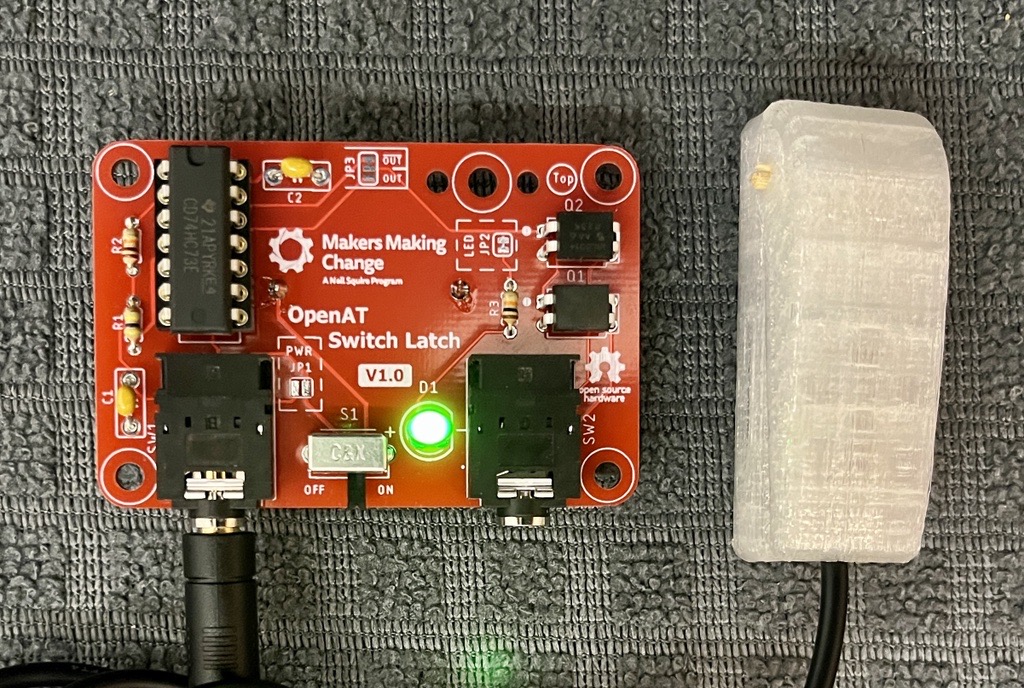
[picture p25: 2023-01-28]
Documentation/Working_Documents/Photos/OpenAtSwitchLatchV1pt0_populatedPCB.png

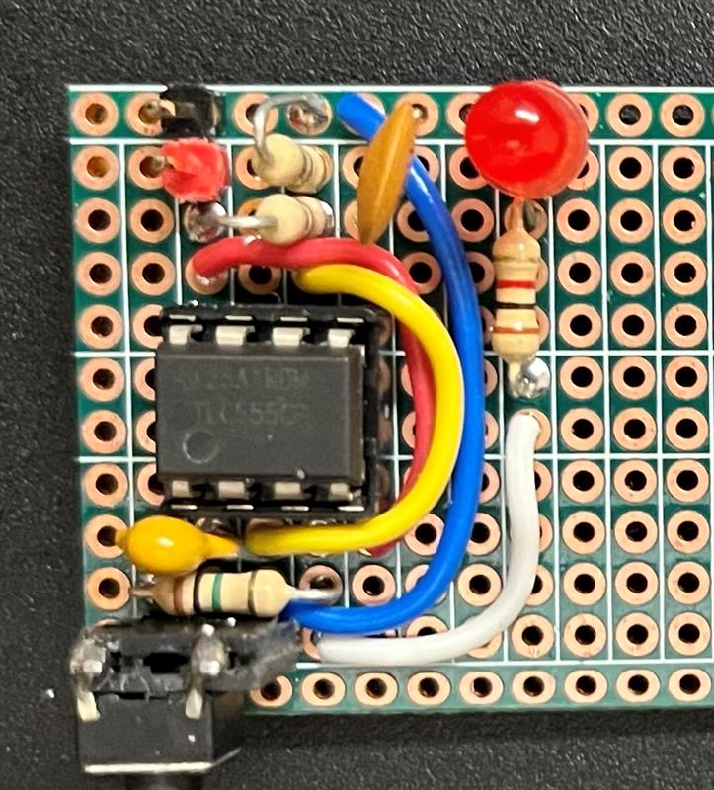
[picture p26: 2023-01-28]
Documentation/Working_Documents/Photos/555_toggle.jpg

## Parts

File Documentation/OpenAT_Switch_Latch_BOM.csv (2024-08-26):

OpenAT Switch Latch
Version: | V1.2.1
Last Updated: | 2024-Aug-26
 |  |  |  |  |  |  |  | Total filament (g) |  | Unit Cost | Total Estimated Cost | Build Cost
 |  |  |  |  |  |  |  | 27.3 |  | $36.91 | $62.86
ID | Commercial Parts |  |  |  |  |  |  |  |  | $30.41 | $33.16
 | Part | Description |  | Manufacturer | Supplier | QTY / Device | QTY / PKG | PKGs | $/ PKG | $ / Device | Total Estimated Cost |  | Link
10 | U1 | CD74HC73E JK Flip Flop |  |  |  | 1 | 1 | 1 | $0.94 | $0.94 | $0.94 |  | https://www.digikey.ca/en/products/detail/texas-instruments/CD74HC73E/1507453
9 | Q1,Q2 | IRLD014PBF 60V 1.2A MOSFET |  |  |  | 2 | 1 | 2 | $2.25 | $4.50 | $4.50 |  | https://www.digikey.ca/en/products/detail/vishay-siliconix/IRLD014PBF/812481
8 | SW1,SW2 | SJ-3566AN 3.5mm Jack Stereo |  |  |  | 2 | 1 | 2 | $2.80 | $5.60 | $5.60 |  | https://www.digikey.ca/en/products/detail/cui-devices/SJ-3566AN/305112
2 | R1 | 470 kOhms 1/8W Through Hole Resistor |  |  |  | 1 | 1 | 1 | $0.15 | $0.15 | $0.15 |  | https://www.digikey.ca/en/products/detail/stackpole-electronics-inc/CF18JT470K/1741719
3 | R2 | 22 kOhms 1/8W Through Hole Resistor |  |  |  | 1 | 1 | 1 | $0.15 | $0.15 | $0.15 |  | https://www.digikey.ca/en/products/detail/stackpole-electronics-inc/CF18JT22K0/1741643
4 | R3 | 10 kOhms 1/8W Through Hole Resistor |  |  |  | 1 | 1 | 1 | $0.15 | $0.15 | $0.15 |  | https://www.digikey.ca/en/products/detail/stackpole-electronics-inc/CF18JT10K0/1741566
5 | C1 | 0.1 µF ±10% Capacitor |  |  |  | 1 | 1 | 1 | $0.46 | $0.46 | $0.46 |  | https://www.digikey.ca/en/products/detail/kemet/C315C104M5U5TA/817927
6 | C2 | 1 µF ±10% Capacitor |  |  |  | 1 | 1 | 1 | $1.15 | $1.15 | $1.15 |  | https://www.digikey.ca/en/products/detail/kemet/C315C105K3R5TA/3726118
13 | BAT1 | 20 mm Coin Cell Battery Holder |  |  |  | 1 | 1 | 1 | $1.69 | $1.69 | $1.69 |  | https://www.digikey.ca/en/products/detail/mpd-memory-protection-devices/BS-7/389447
11 | D1 | 5 mm Green LED |  |  |  | 1 | 1 | 1 | $0.46 | $0.46 | $0.46 |  | https://www.digikey.ca/en/products/detail/creeled-inc/C5SMF-GJE-CX14Q7T2/4794039
7 | S1 | Slide Switch |  |  |  | 1 | 1 | 1 | $0.75 | $0.75 | $0.75 |  | https://www.digikey.ca/en/products/detail/c-k/OS102011MA1QS1/1981431
19 |  | #4-3/8" Pan Head Screw |  |  |  | 6 | 1 | 6 | $0.61 | $3.66 | $3.66 |  | https://www.digikey.ca/en/products/detail/serpac/6005/307599
14 |  | Coin Cell Battery, CR2032 |  |  |  | 1 | 2 | 1 | $5.50 | $2.75 | $5.50
 |  | Digikey Shipping |  |  |  | 1 | 1 | 1 | $8.00 | $8.00 | $8.00
 | Custom PCB |  |  |  |  |  |  |  |  | $5.80 | $29.00
 | Part | Description |  | Manufacturer | Supplier | QTY / Device | QTY / PKG | PKGs | $/ PKG | $ / Device | Total Estimated Cost |  | Link
1 | PCB1 | Custom PCB |  |  |  | 1 | 5 | 1 | $4.00 | $0.80 | $4.00
 | Shipping | Economical Global Direct Line |  |  |  | 1 | 5 | 1 | $25.00 | $5.00 | $25.00
 | 3D Printed Parts |  |  |  |  |  |  | 27.3 |  | $0.70 | $0.70
 | Part | Description | Filament Type | Filament | Color | QTY / Device | Mass (g) / Part | Total Mass | $ / kg | $ / Device | Total Estimated Cost |  | Link
15 |  | Enclosure Top | PLA |  | Any | 1 | 11.4 | 11.4 | $25.00 | $0.29 | $0.29
17 |  | Enclosure Bottom | PLA |  | Any | 1 | 11.4 | 11.4 | $26.00 | $0.30 | $0.30
18 |  | Battery Cover | PLA |  | Any | 1 | 3.3 | 3.3 | $27.00 | $0.09 | $0.09
16 |  | Switch Slide | PLA |  | Any | 1 | 0.7 | 0.7 | $28.00 | $0.02 | $0.02
12 |  | LED Spacer | PLA |  | Any | 1 | 0.5 | 0.5 | $29.00 | $0.01 | $0.01
 | Tools
 | Tool | Description |  | Manufacturer | Supplier |  |  |  |  |  |  |  | Link
 | Screwdriver | Medium Phillips
 | Needle nose pliers
 | Side Cutters
 | Soldering Iron
 | Solder | 60/40 rosin core solder for electronics
 | Multimeter
 | Alternatives
 | Part | Description |  | Manufacturer | Supplier | QTY / Device | QTY / PKG | PKGs | $/ PKG | $ / Device | Total Estimated Cost |  | Link

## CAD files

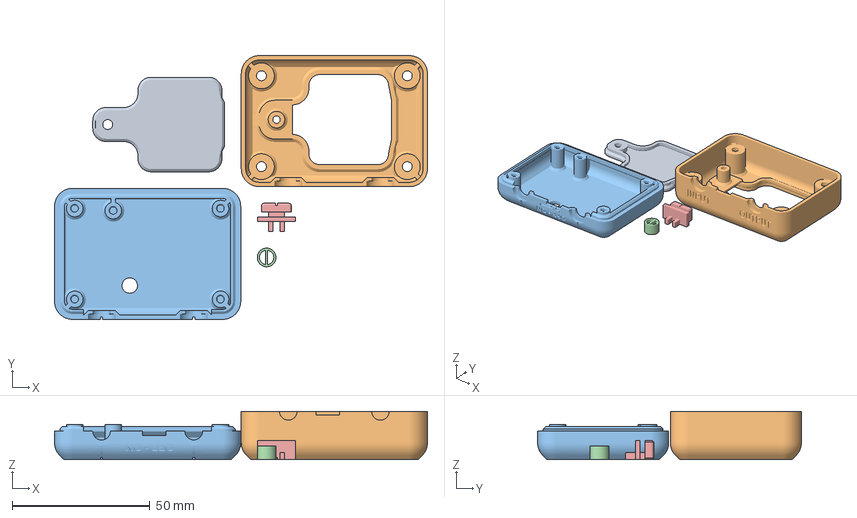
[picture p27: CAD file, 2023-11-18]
Build_Files/3D_Printing_Files/OpenAT_Switch_Latch_v54.3mf
135.6 x 95.9 x 17.6 mm
Battery_Cover.stl
Enclosure_Bottom.stl
Enclosure_Top.stl
LED_Spacer.stl
Switch_Slide.stl

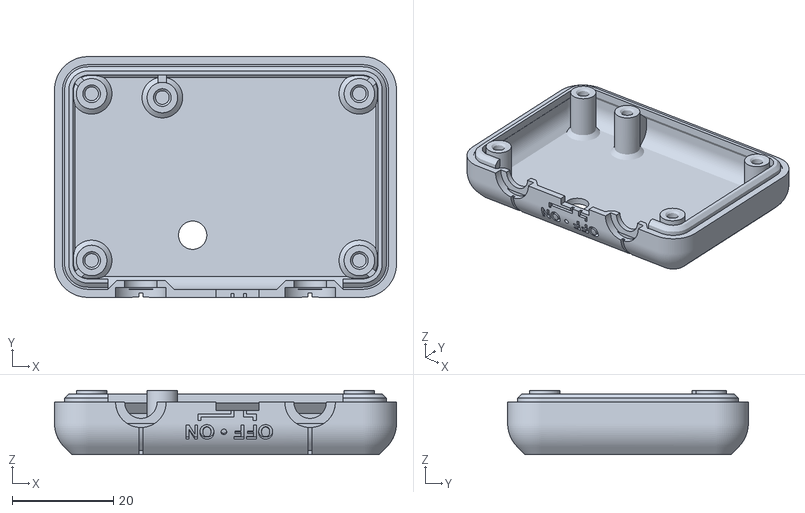
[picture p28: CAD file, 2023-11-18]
Build_Files/3D_Printing_Files/Enclosure_Top.stl
67.7 x 47.6 x 12.7

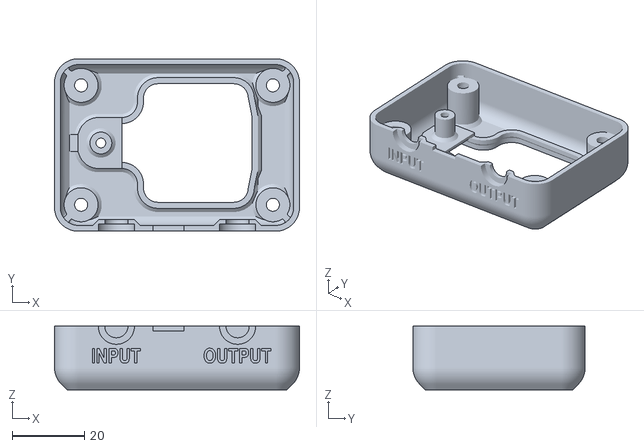
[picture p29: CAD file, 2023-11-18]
Build_Files/3D_Printing_Files/Enclosure_Bottom.stl
67.7 x 47.6 x 17.6

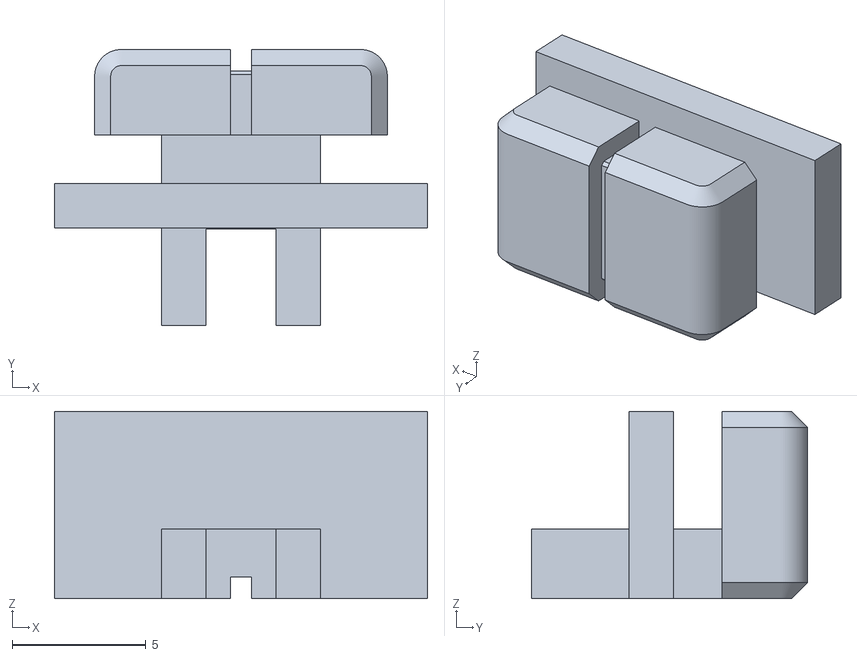
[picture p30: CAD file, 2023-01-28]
Build_Files/3D_Printing_Files/Switch_Slide.stl
13.9 x 10.3 x 7.00

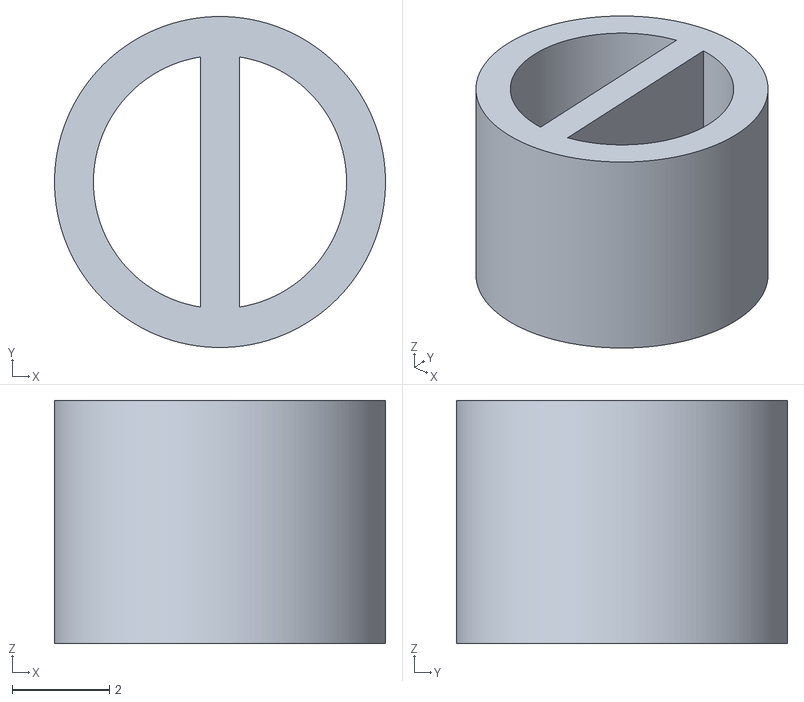
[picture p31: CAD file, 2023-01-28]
Build_Files/3D_Printing_Files/LED_Spacer.stl
6.80 x 6.80 x 5.00

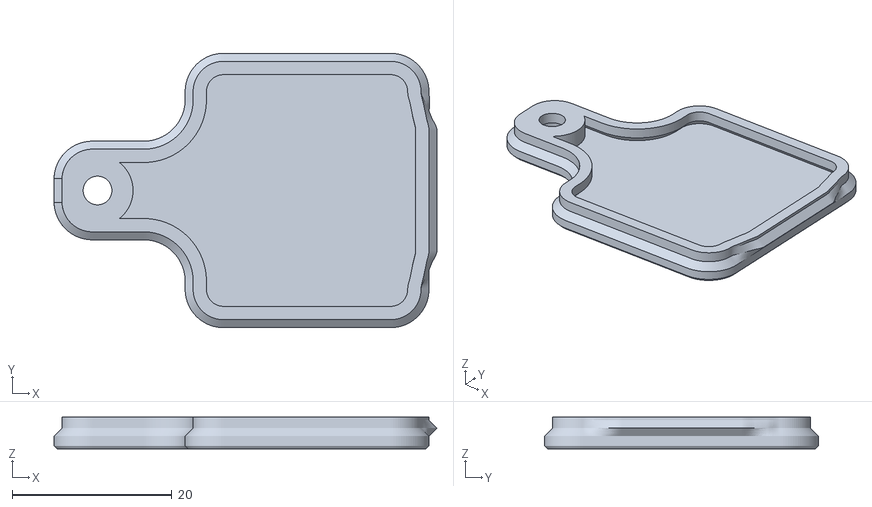
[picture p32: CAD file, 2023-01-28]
Build_Files/3D_Printing_Files/Battery_Cover.stl
48.0 x 34.4 x 4.00

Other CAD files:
Build_Files/3D_Printing_Files/OpenAT-Switch-Latch_Set.stl

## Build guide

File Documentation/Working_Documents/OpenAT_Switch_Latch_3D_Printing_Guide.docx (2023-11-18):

# 3D Printing Summary

Metrics | Individual Parts | Set
Total Print Time (min) | 2:34 | 2:40
Total Number of Components | 5 | 5
Typical Total Mass (g) | 28 | 28
Typical Number of Print Setups | 5 | 1

# Customization Options

The enclosure can be printed in the user’s desired colour. The Switch Slide can be printed in a contrasting color from the Enclosure Top and Enclosure Bottom to make it easier to see.

# 3D Printing Settings

## Individual Parts

Print File Name | Qty | Total Print Time (hr:min) | Mass (g) | Infill (%) | Support(Y/N) | Layer Height/ Nozzle Diameter(mm) | Notes
Enclosure Top | 1 | 1:05 | 11.4 | 20 | N | 0.2/0.4
Enclosure Bottom | 1 | 1:05 | 11.4 | 20 | N | 0.2/0.4
Battery Cover | 1 | 0:15 | 3.3 | 20 | N | 0.2/0.4
Switch Slide | 1 | 0:07 | 0.7 | 20 | N | 0.2/0.4
LED Spacer | 1 | 0:02 | 0.5 | 20 | N | 0.2/0.4 | Optional; Recommended

## Set

Print File Name | Qty | Total Print Time (hr:min) | Mass (g) | Infill (%) | Support(Y/N) | Layer Height/ Nozzle Diameter(mm) | Notes
OpenAT-Switch-Latch_Set.stl | 1 | 2:40 | 28 | 20 | N | 0.2/0.4

# Post-Processing

Some post-processing may be required on the Enclosure Bottom where the battery cover screw attached to clean up any bridging that wasn’t successful.

# Examples of Quality Prints

Enclosure Top

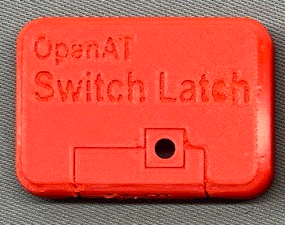
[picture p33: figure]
3-D printed enclosure top showing clear lettering

Enclosure Bottom

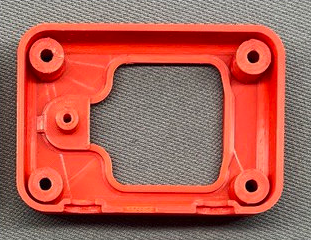
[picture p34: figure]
3-D printed enclosure bottom

Battery Cover

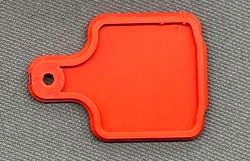
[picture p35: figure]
3d-printed battery cover

Switch Slide

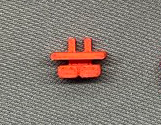
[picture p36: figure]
3-D printed switch slide

LED Spacer

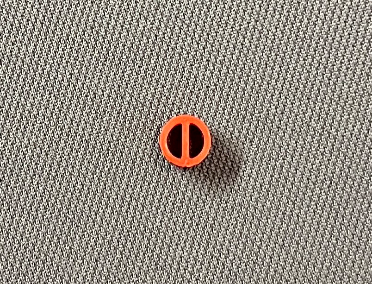
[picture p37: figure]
3-D printed L-E-D spacer

© 2023 by Neil Squire / Maker Making Change. This work is licensed under the CC BY SA 4.0 License: http://creativecommons.org/licenses/by-sa/4.0 Files available at https://makersmakingchange.com/project/OpenAT-Switch-Latch/ Page 1 of 2

V1.0 | DECEMBER 2022 OpenAT Switch Latch 3D Printing Guide

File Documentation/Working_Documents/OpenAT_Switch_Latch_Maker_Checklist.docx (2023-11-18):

# Maker To Do List

- Read through the Assembly Guide to become familiar with required components, tools, supplies, and safety gear and overall assembly steps.
- Talk to User about customization options (e.g., color, any special requests, etc.)
- Order custom PCBs
- Order hardware components
- Gather tools, supplies, and safety equipment.
- Assemble the device.
- Test device
- Print “User Guide”

# Items to Give to User

- Assembled, tested device.
- “User Guide”

© 2023 by Neil Squire / Makers Making Change. This work is licensed under the CC BY SA 4.0 License: http://creativecommons.org/licenses/by-sa/4.0 Files available at https://makersmakingchange.com/project/OpenAT-Switch-Latch/ Page 1 of 1

V1.0 | December 2022 OpenAT-Switch-Latch Maker Checklist

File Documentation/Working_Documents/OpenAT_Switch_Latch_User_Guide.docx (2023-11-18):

## Introduction

The OpenAT Switch Latch enables a momentary assistive switch input to toggle on and off control of an attached Switch Adapted output device.

## Features

Power Switch:

Input Jack: Connection for Assistive Switch (3.5 mm).

LED: When lit, the LED indicates the Output Jack is enabled (i.e., circuit is closed).

Output Jack: Connection for Switch Adapted device being controlled.

Battery hatch: (case bottom) The single screw battery hatch allows easy changing of the CR2032 battery.

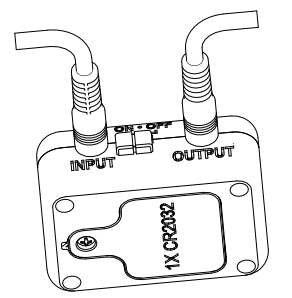
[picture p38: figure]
Diagram illustrating main features of Switch latch. The Switch Latch is a rectangular box. On the top, an indicator light turns on when the output is enabled. On the front, there is an input switch jack on the left, a sliding power switch in the middle and an output jack on the left. The power swi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

Input Jack

Output Jack

Power Switch Jack

LED

Battery hatch Jack

## Usage

To use the Switch Latch, a momentary switch is plugged into the 3.5 mm input jack. A switch adapted device is then plugged into the 3.5 mm output jack. The power switch must be enabled to use the device. However, the device will turn itself off if there is no plug inserted into the input jack.

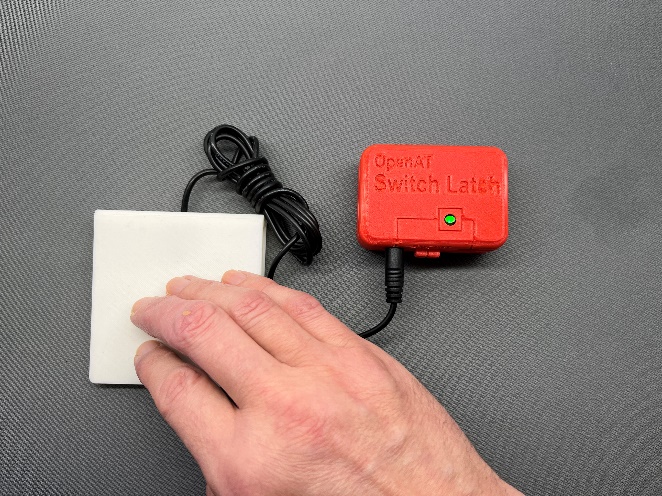
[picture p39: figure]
A person pressing an assistive switch connected to the input of the Switch Latch, causing the L-E-D light to illuminate.

## Compatibility

Both inputs and outputs are compatible with standard 3.5 mm assistive switches and the devices they typically control.

## Specifications

- Dimensions: 67.5 mm x 47.5 mm x 28mm
- Weight: 45 g
- Power Consumption: 112uA (0.11ma) on, 4uA standby (LED off).
- Battery: 1X CR2032

## Changing Battery

To change the battery, use a screwdriver to loosen the single screw on the battery hatch. Remove and dispose of the old battery properly. Install the new battery and reinstall the battery hatch.

## Cleaning

Device may be cleaned by wiping it with a damp cloth. Do not submerge the device. Do not expose to high heat (e.g., dishwasher)

© 2023 by Neil Squire / Makers Making Change. This work is licensed under the CC BY SA 4.0 License: http://creativecommons.org/licenses/by-sa/4.0 Files available at https://makersmakingchange.com/project/OpenAT-Switch-Latch/ Page 2 of 3

V1.0 | January 2023 OpenAT-Switch-Latch user Quick Guide

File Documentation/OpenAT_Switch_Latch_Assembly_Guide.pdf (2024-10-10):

V1.2.2 | October 2024

## OpenAT Switch Latch

## ASSEMBLY GUIDE

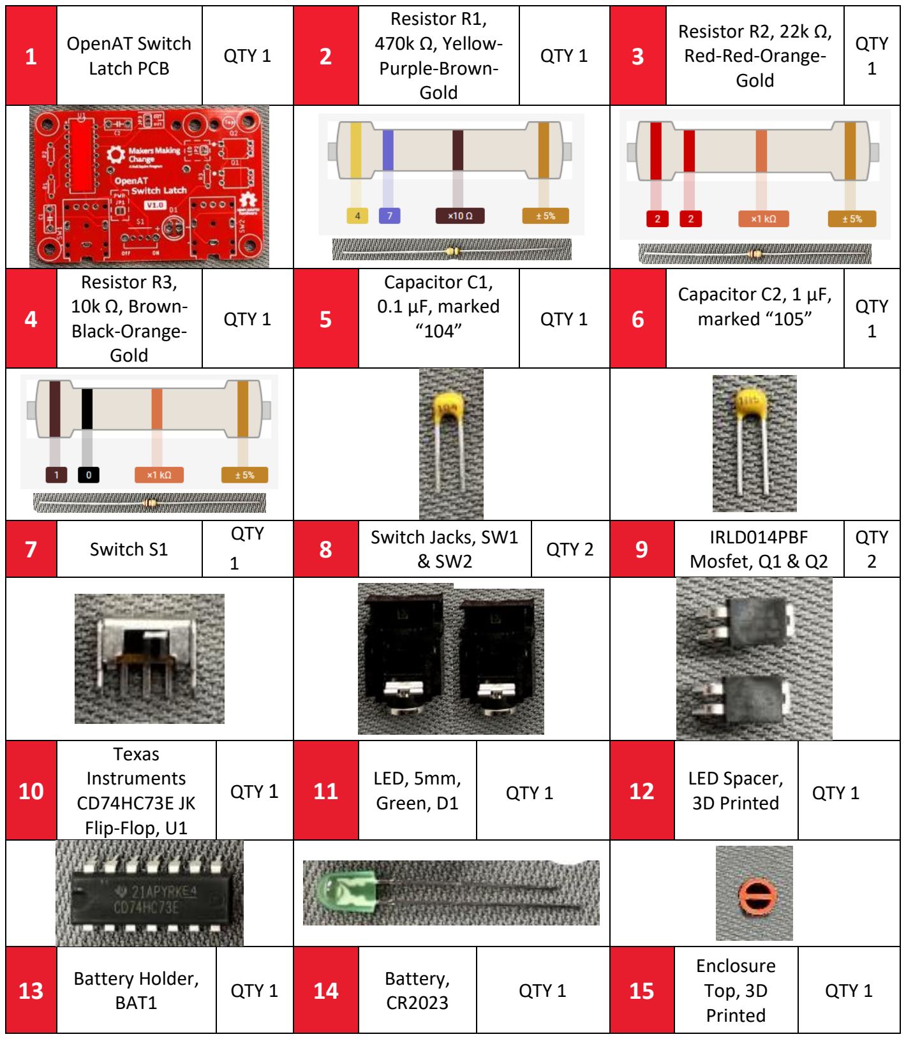
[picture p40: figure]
OpenAT Switch; Latch PCB; QTY 1; Resistor R1, 470k Ω, Yellow- Purple-Brown- Gold; Resistor R2, 22k Ω, Red-Red-Orange- Gold; Resistor R3, 10k Ω, Brown- Black-Orange- Gold; Capacitor C1, 0.1 µF, marked; Capacitor C2, 1 µF,; marked “105”; QTY; 7 Switch S1; QTY 119; Switch Jacks, SW1; QTY 2; IRLD014PBF Mosfet, Q1 & Q2; Texas Instruments CD74HC73E JK Flip-Flop, U1; LED, 5mm,; Green, D1; LED Spacer,; 3D Printed; 13 Battery Holder,; BAT1; Battery,; Enclosure Top, 3D Printed

© 2023-2024 by Neil Squire / Makers Making Change. This work is licensed under the CC BY SA 4.0 License: http://creativecommons.org/licenses/by-sa/4.0
Files available at https://makersmakingchange.com/project/OpenAT-Switch-Latch/ | Page 1 of 22

### Required Components

## ASSEMBLY GUIDE

16 Switch Slide, 3D; Printed; QTY 1; Enclosure Bottom, 3D Printed; Battery Cover, 3D Printed; Screw, #4, 3/8” length, Pan- Head, Sheet metal; QTY 6

Files available at https://makersmakingchange.com/project/OpenAT-Switch-Latch/ | Page 2 of 22

### Required Tools

- Screwdriver Medium Phillips
- Needle nose pliers
- Side Cutters
- Soldering Iron
- 60/40 rosin core solder for electronics
- Multimeter
- Assistive Switch with 3.5 mm cable for testing
- Optional: Tape / reusable putty-like adhesive (e.g., BLUE TACK) for helping position components while soldering

### Required Personal Protective Equipment (PPE)

- Safety glasses
- Vinyl gloves (if skin sensitivity to rosin or have dermatitis)

## ASSEMBLY GUIDE

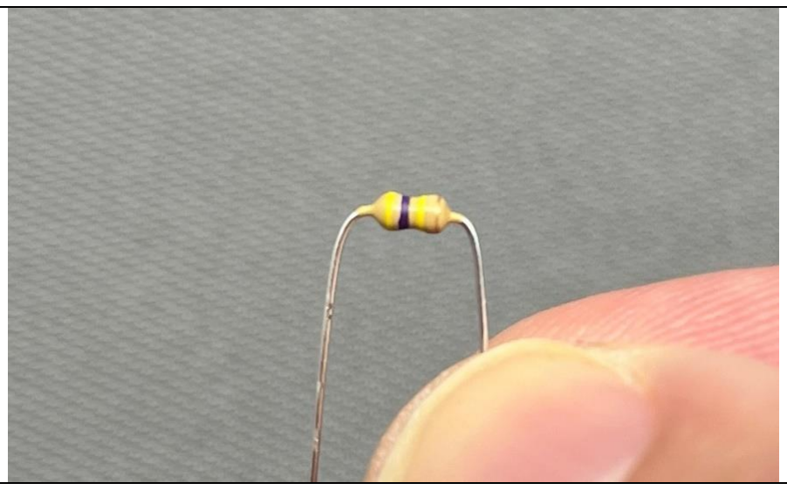
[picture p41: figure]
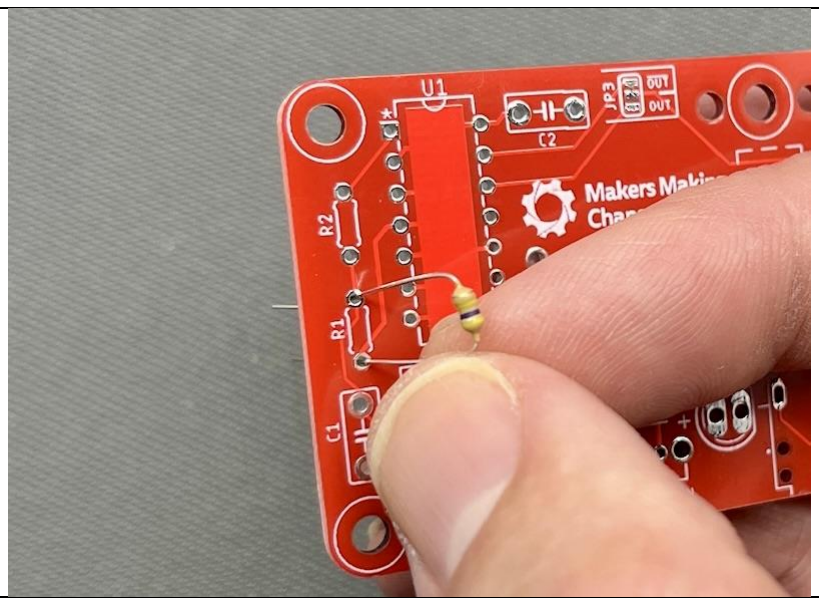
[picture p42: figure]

Files available at https://makersmakingchange.com/project/OpenAT-Switch-Latch/ | Page 3 of 22

### Assembly Instructions

### Step 1: Identify and Prep Resistor R1

Identify the 470K resistor (Colour code stripes: Yellow, Violet, Yellow). Bend both leads of the resistor straight down, so that it appears like in the photo below.

### Step 2: Insert Resistor R1 into PCB

Insert the 470K resistor (Colour code stripes: Yellow, Violet, Yellow) into the holes marked “R1” on the PCB. Ensure the body of the resistor is flat against the circuit board. Bending the wires apart once it’s in position will help keep it in place during soldering.

## ASSEMBLY GUIDE

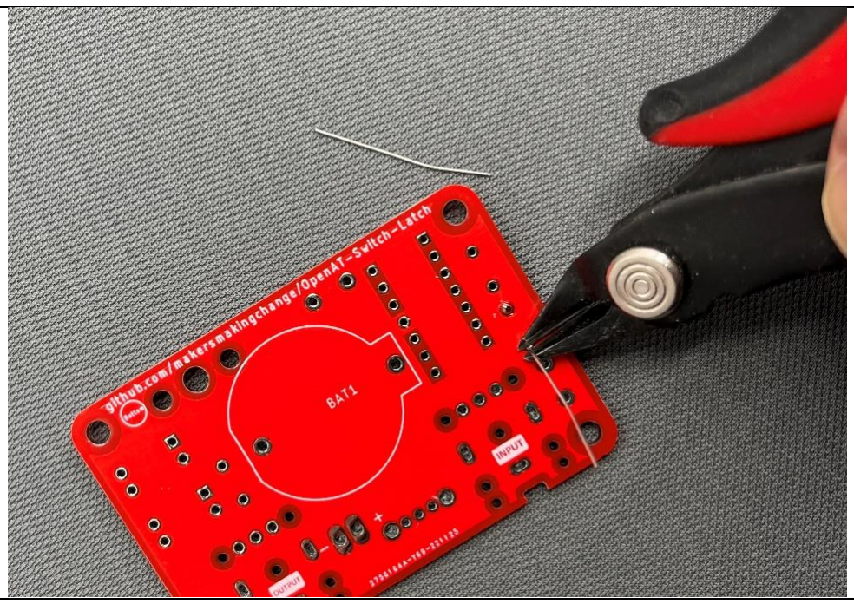
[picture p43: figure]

Files available at https://makersmakingchange.com/project/OpenAT-Switch-Latch/ | Page 4 of 22

### Step 3: Solder Resistor R1 leads

Flip over the PCB and solder the two wires of resistor R1 to the circuit board.

### Step 4: Trim Resistor R1 leads

When joints are soldered, trim the wire ends with the flat side of side cutters. Trim right on top of the solder peak.

## ASSEMBLY GUIDE

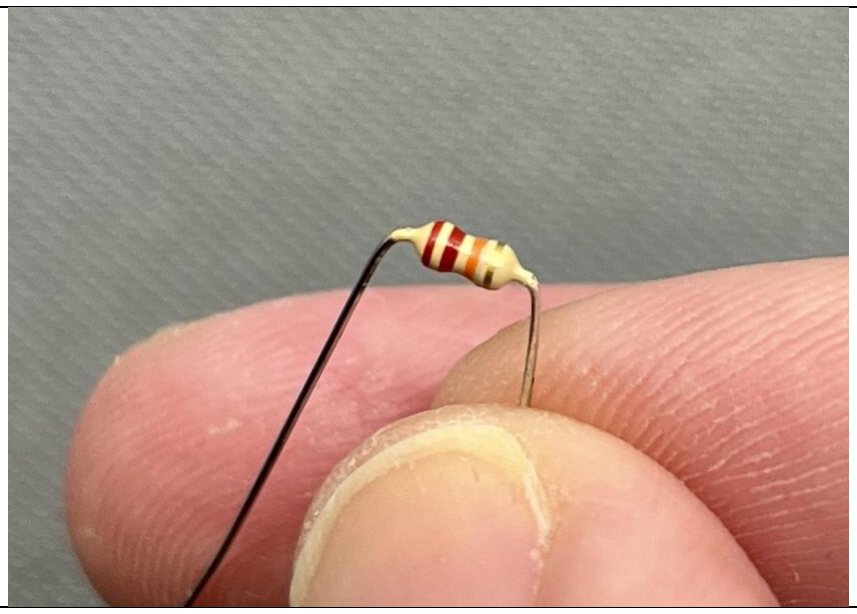
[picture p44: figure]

Files available at https://makersmakingchange.com/project/OpenAT-Switch-Latch/ | Page 5 of 22

### Step 5: Identify and prep Resistor R2

Identify the 22K resistor (Colour code stripes: Red, Red, Orange). Bend the wire leads straight down, as before, in preparation for soldering.

### Step 6: Insert Resistor R2 into PCB

Insert the 22K resistor (Colour code stripes: Red, Red, Orange) into the holes marked “R2” on the PCB. Again, bend the leads after, to keep it in place during soldering.

## ASSEMBLY GUIDE

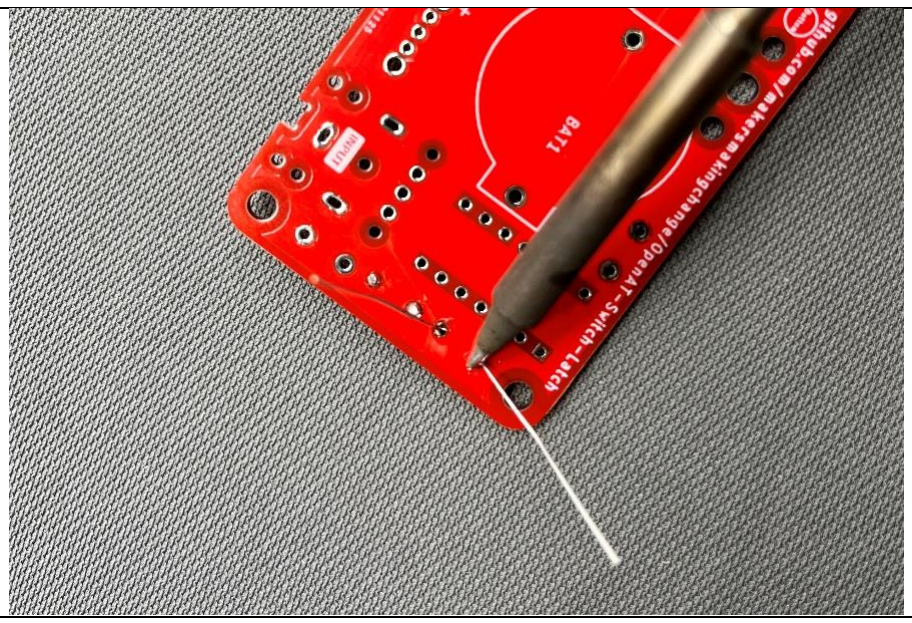
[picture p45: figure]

Files available at https://makersmakingchange.com/project/OpenAT-Switch-Latch/ | Page 6 of 22

### Step 7: Solder and trim Resistor R2 leads

Solder the two wires. When done, trim the wire ends with side cutters, as before.

### Step 8: Identify and prep Resistor R3

Identify the 10K resistor (Colour code stripes: Brown, Black, Orange). As with the previous resistors, bend the wires straight down.

## ASSEMBLY GUIDE

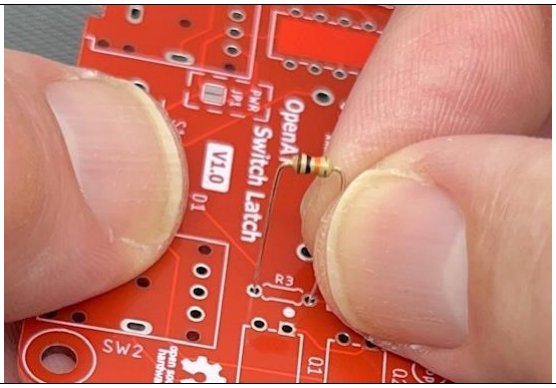
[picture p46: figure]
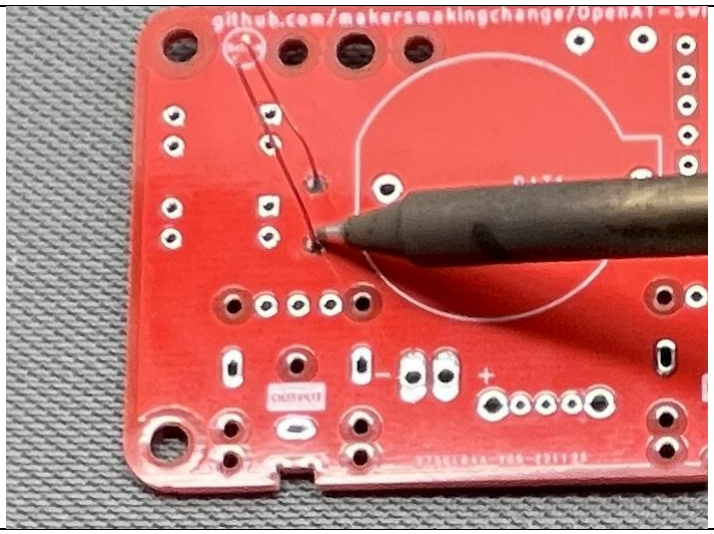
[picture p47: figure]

Files available at https://makersmakingchange.com/project/OpenAT-Switch-Latch/ | Page 7 of 22

### Step 9: Insert Resistor R3 Into PCB

Insert the 10K resistor (Colour code stripes: Brown, Black, Orange) into the holes marked “R3” on the PCB. Once again, bend the wires apart.

### Step 10: Solder and trim Resistor R3 leads

Solder the two wires. When done, trim the wire ends with side cutters.

## ASSEMBLY GUIDE

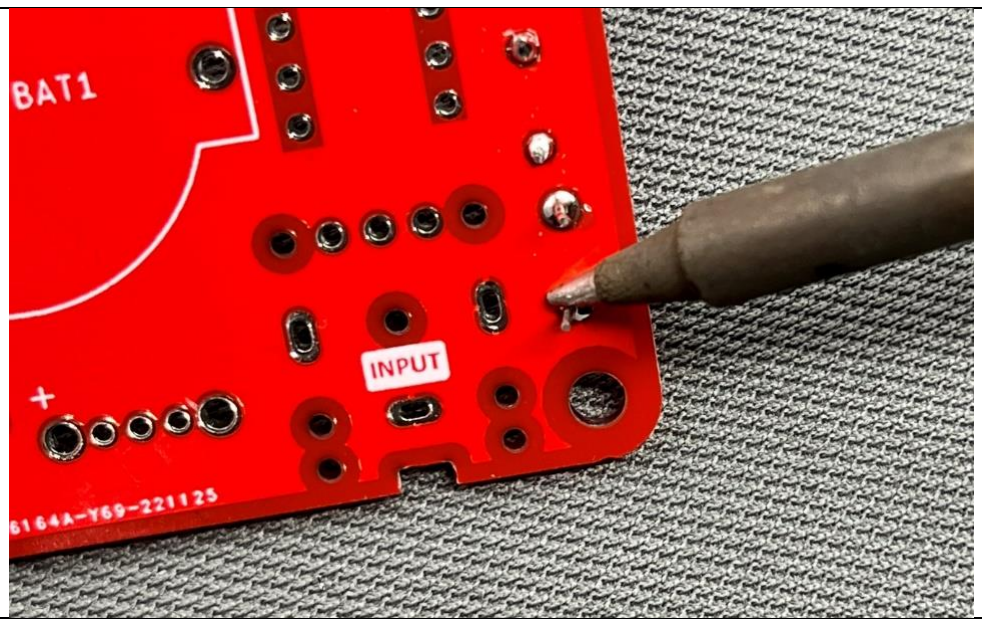
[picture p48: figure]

Files available at https://makersmakingchange.com/project/OpenAT-Switch-Latch/ | Page 8 of 22

### Step 11: Identify and insert Capacitor C1 into PCB

Insert 0.1uF capacitor (the smaller capacitor marked “104”) into holes for location C1 on the PCB.

### Step 12: Solder and trim Capacitor C1 leads

Solder the two leads. When done, trim the wire ends with side cutters.

## ASSEMBLY GUIDE

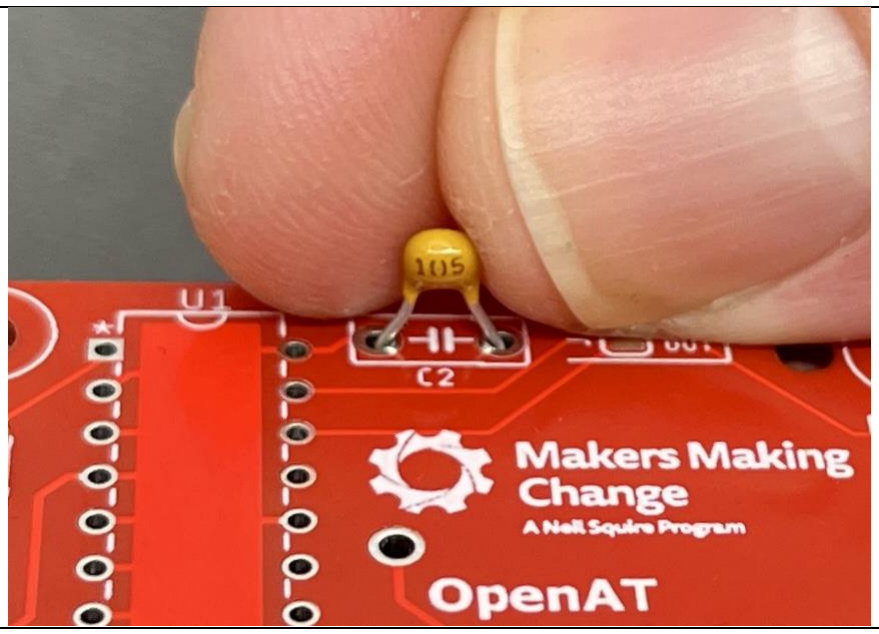
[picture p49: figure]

Files available at https://makersmakingchange.com/project/OpenAT-Switch-Latch/ | Page 9 of 22

### Step 13: Identify and insert Capacitor C2 into PCB

Insert 1uF capacitor (the larger capacitor marked “105”) into holes for location C2 on the PCB.

### Step 14: Solder and trim Capacitor C2 leads

Solder the two leads. When done soldering, trim the wire ends using side cutters.

## ASSEMBLY GUIDE

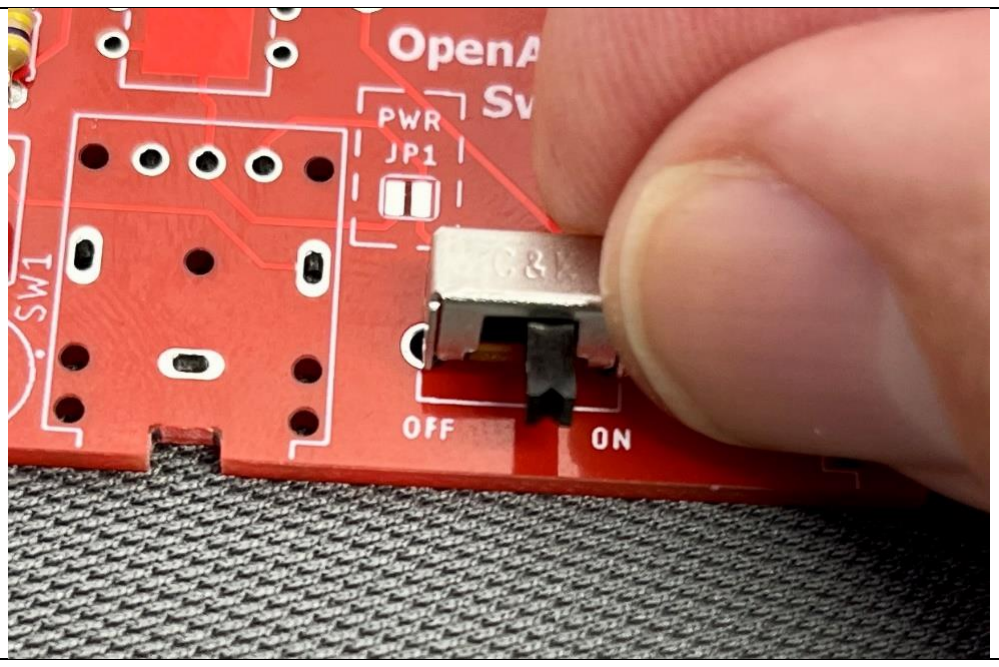
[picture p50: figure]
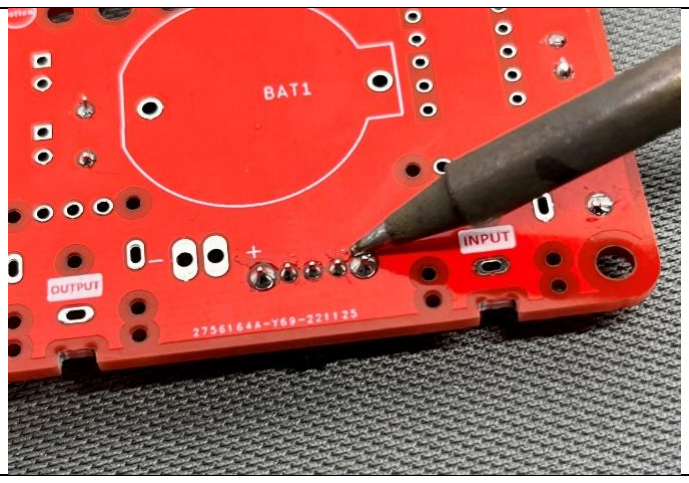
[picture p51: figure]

Files available at https://makersmakingchange.com/project/OpenAT-Switch-Latch/ | Page 10 of 22

### Step 15: Insert Switch S1 into the PCB

Insert the Switch into location S1 on the circuit board. Ensure the switch toggle is facing towards the edge of the board as shown below. To aid in soldering (next step), it may help to use tape or Blue Tack to hold the switch in position.

### Step 16: Solder S1 pins

Solder the switch into place by soldering middle terminal first. Confirm the switch is aligned on the component side of the board, and then solder the remaining 4 pins.

## ASSEMBLY GUIDE

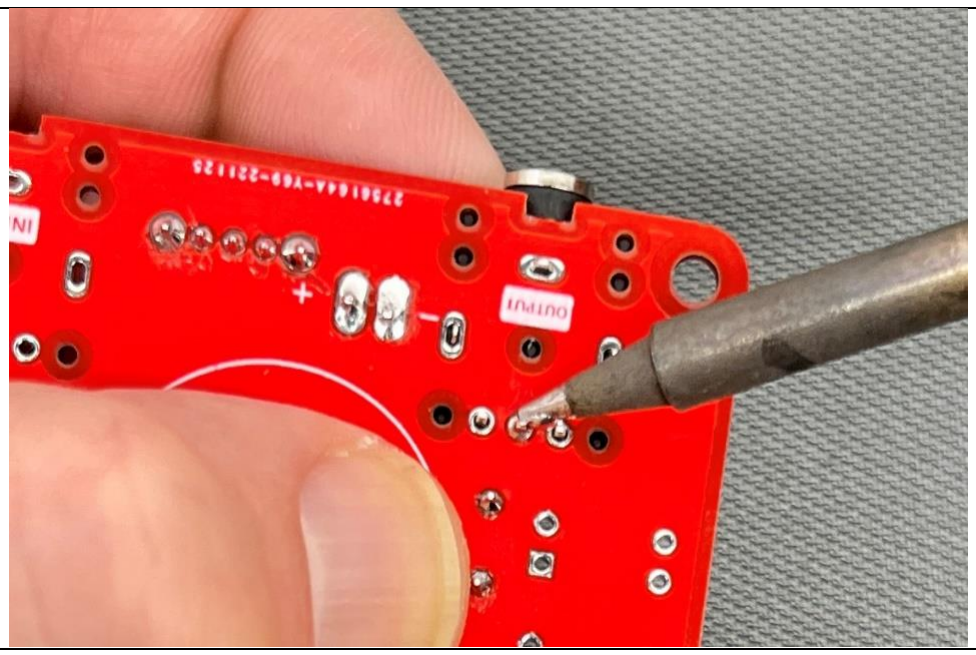
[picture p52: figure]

Files available at https://makersmakingchange.com/project/OpenAT-Switch-Latch/ | Page 11 of 22

### Step 17: Insert switch Jacks SW1 and SW2 into PCB

Insert both jacks into positions SW1 and SW2 (shown). Jacks should be held in place during soldering (next step).

### Step 18: Solder SW1 and SW2

Solder one jack pin first. Confirm the jack is properly positioned on the component side of the board, and then solder the remaining pins.

Repeat these steps for the second jack.

## ASSEMBLY GUIDE

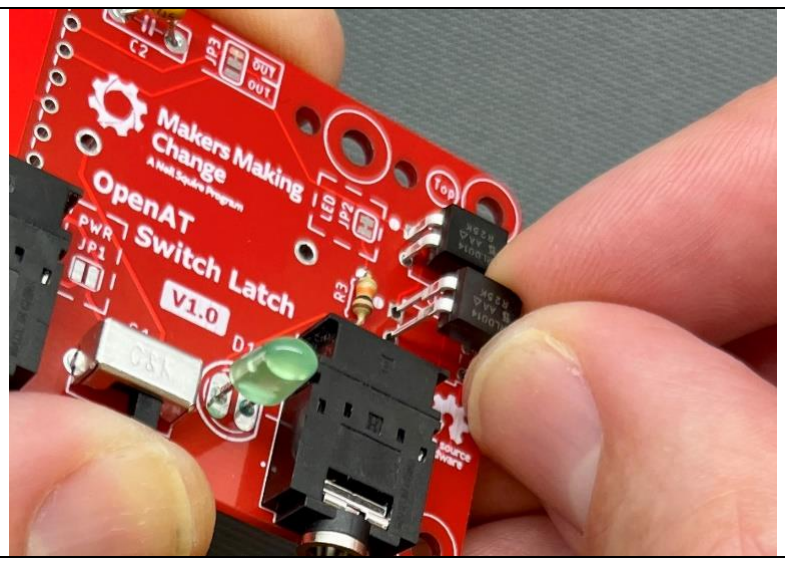
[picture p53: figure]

Files available at https://makersmakingchange.com/project/OpenAT-Switch-Latch/ | Page 12 of 22

### Step 19: Insert MOSFETS Q1 and Q2 into PCB

Insert both MOSFETS into positions marked Q1 and Q2.

IMPORTANT: The MOSFETS are polarized and must be oriented correctly. The tabbed side of the MOSFETS should go in closest to the right edge of the PCB. Note, the pins on the MOSFET may also need to be bent inwards slightly, to fit into the holes of the circuit board.

### Step 20: Solder Q1 and Q2

Solder one MOSFET pin first. Confirm the MOSFET is properly oriented on the component side of the board, and then solder the remaining pins.

Repeat these steps for the second MOSFET.

## ASSEMBLY GUIDE

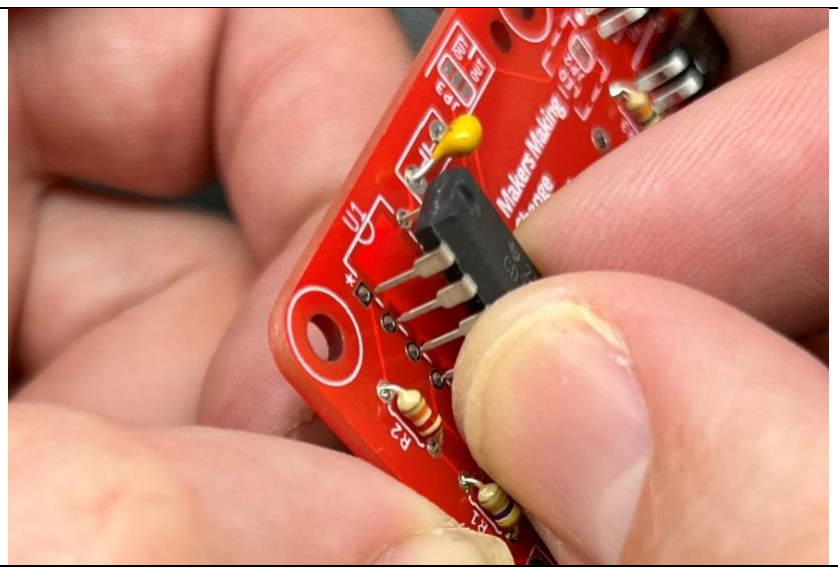
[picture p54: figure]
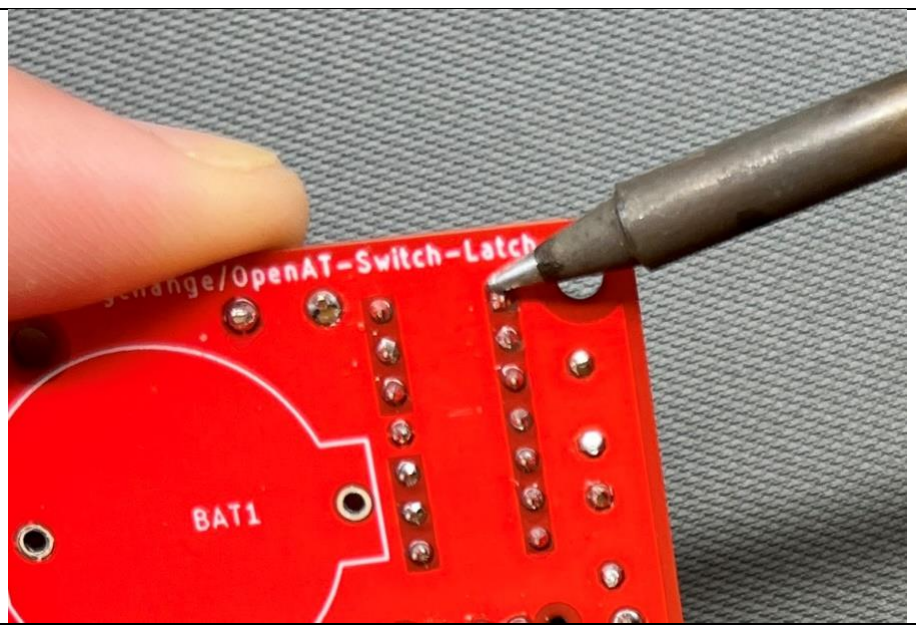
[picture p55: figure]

Files available at https://makersmakingchange.com/project/OpenAT-Switch-Latch/ | Page 13 of 22

### Step 21: Insert IC U1 into the PCB

Insert the IC into position U1. IMPORTANT: The IC polarized and must be oriented correctly. Pin 1 of the IC should go in closest to the left edge of the PCB. Note the physical U-shaped notch on the IC should go over the U-shaped notch printed on the PCB (see photo below). Note, also, the pins of the IC may need to be bent inwards slightly, to fit into the holes of the circuit board.

### Step 22: Solder U1

Solder one IC pin first. Confirm the IC is properly oriented (see previous step). If the IC is positioned correctly, solder the remaining pins. Repeat these steps for the second MOSFET.

## ASSEMBLY GUIDE

Files available at https://makersmakingchange.com/project/OpenAT-Switch-Latch/ | Page 14 of 22

### Step 23: Insert LED through LED Spacer and into PCB

Slide the LED Spacer onto the LED, and then slide the LED into location D1 on the board.

Important! Make sure the 3D printed LED Spacer is placed on the LED leads.

Important! The longer wire of LED (positive lead) MUST be placed into the hole marked + (as shown in

## ASSEMBLY GUIDE

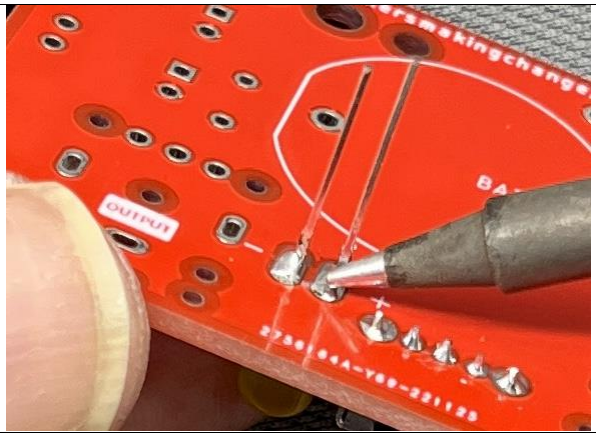
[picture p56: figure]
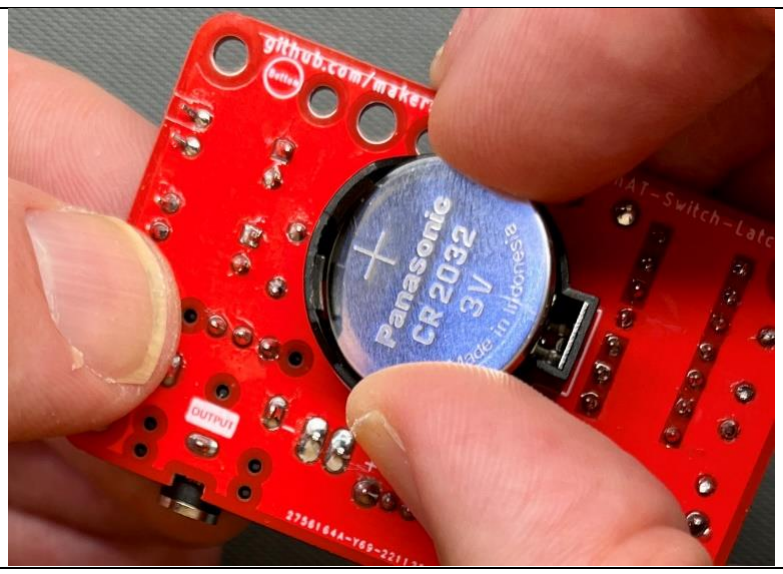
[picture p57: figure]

Files available at https://makersmakingchange.com/project/OpenAT-Switch-Latch/ | Page 15 of 22

### Step 24: Solder and trim LED

Before soldering, hold the LED into position, so that the body of the LED is pressing against the spacer and the circuit board. Solder the LED into place by soldering the longest lead (+) first. Confirm the LED is properly positioned on the component side of the board, and then solder the remaining lead. When soldering is complete, trim off the LED leads with side cutters.

### Step 25: Insert Battery into Battery Holder

Insert a 3V lithium coin cell, type CR2032, into the holder. Ensure the positive (+) side of the battery is facing up, and that the battery is fully inserted.

## ASSEMBLY GUIDE

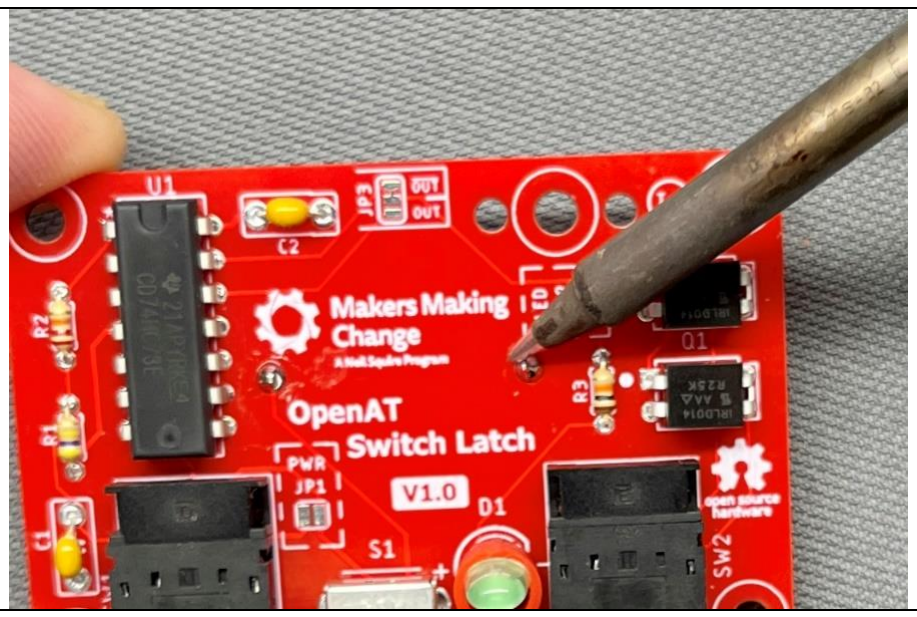
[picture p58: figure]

Files available at https://makersmakingchange.com/project/OpenAT-Switch-Latch/ | Page 16 of 22

### Step 26: Insert Battery Holder into PCB

Insert the battery holder on the solder side of the circuit board. Note the rectangular end of the battery holder should match the corresponding outline printed on the circuit board.

### Step 27: Solder Battery Holder pins

Solder one battery holder pin first. Battery holder should match the corresponding outline printed on the circuit board. Then solder the second battery holder pin.

## ASSEMBLY GUIDE

Files available at https://makersmakingchange.com/project/OpenAT-Switch-Latch/ | Page 17 of 22

### Step 28: Preliminary Test with Assistive Switch

Insert the 3.5 mm plug end of an assistive switch into the input jack. Turn on the power switch (move switch toggle right). Activate the assistive switch. The LED should turn on (or off), and stay that way, until the next assistive switch activation.

If the LED doesn’t operate as expected, stop and troubleshoot before proceeding to the next step.

## ASSEMBLY GUIDE

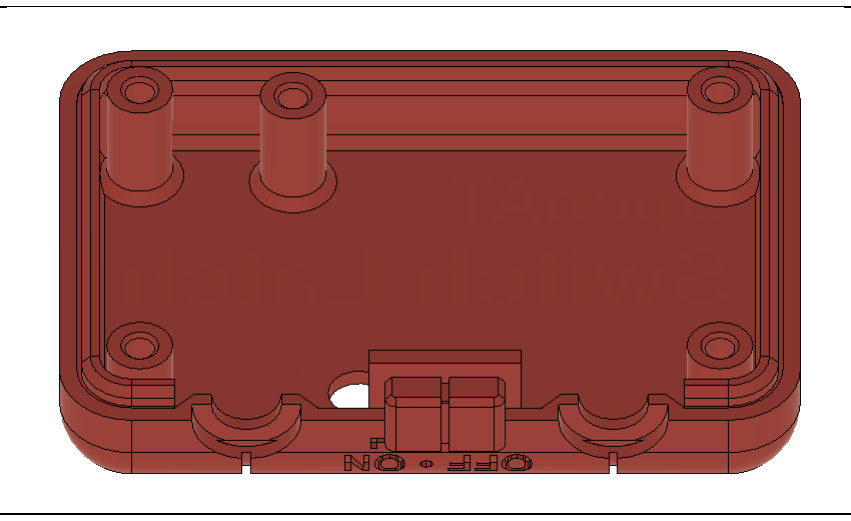
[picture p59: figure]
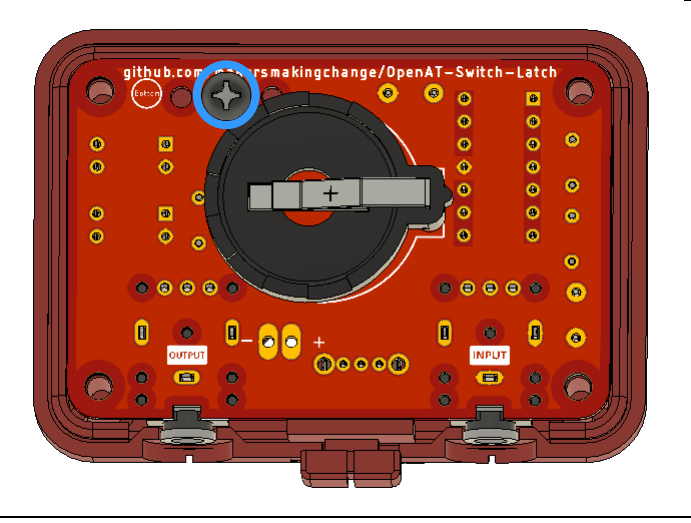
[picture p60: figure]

Files available at https://makersmakingchange.com/project/OpenAT-Switch-Latch/ | Page 18 of 22

### Step 29: Insert Switch Slide into Enclosure Top

Position the Enclosure Top with the ‘OpenAT Switch Latch’ logo facing down. Insert the Switch Slide into the groove and slide it into the off position.

### Step 30: Secure PCB into Enclosure Top

Flip the PCB so the bottom side is face up and insert into the Enclosure Top, aligning the LED with the hole. Secure with ONE #4-3/8” screw in the hole beside the battery holder.

## ASSEMBLY GUIDE

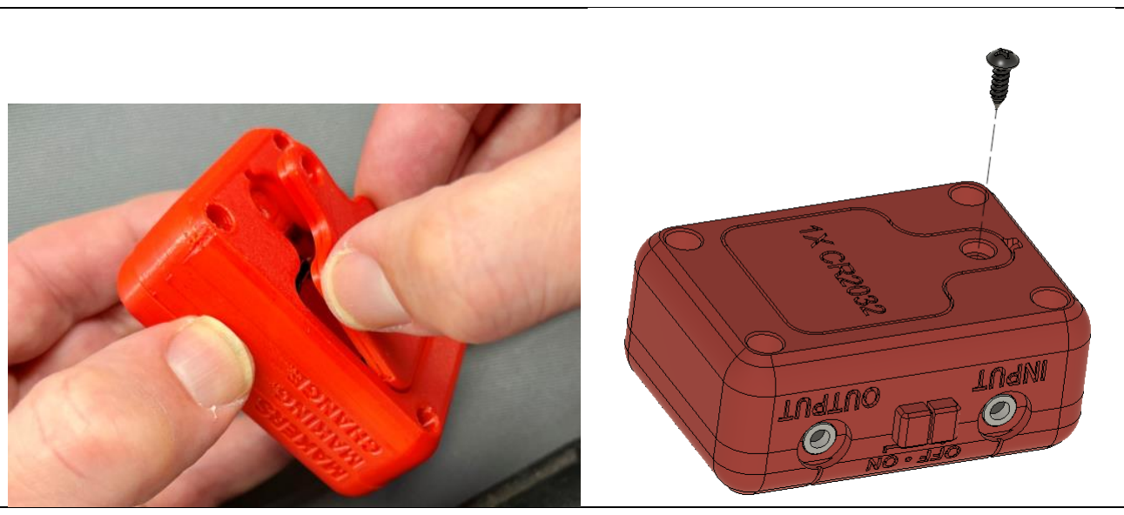
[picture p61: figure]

Files available at https://makersmakingchange.com/project/OpenAT-Switch-Latch/ | Page 19 of 22

### Step 31: Secure Enclosure Bottom to Enclosure Top

Line up the Enclosure Bottom over the Enclosure Top. Fasten with FOUR #4 x 3/8” screws.

### Step 32: Attach and Secure Battery Cover to Enclosure Bottom

Insert the Battery Cover into the Enclosure Bottom. Secure with ONE #4 x 3/8” screw.

## ASSEMBLY GUIDE

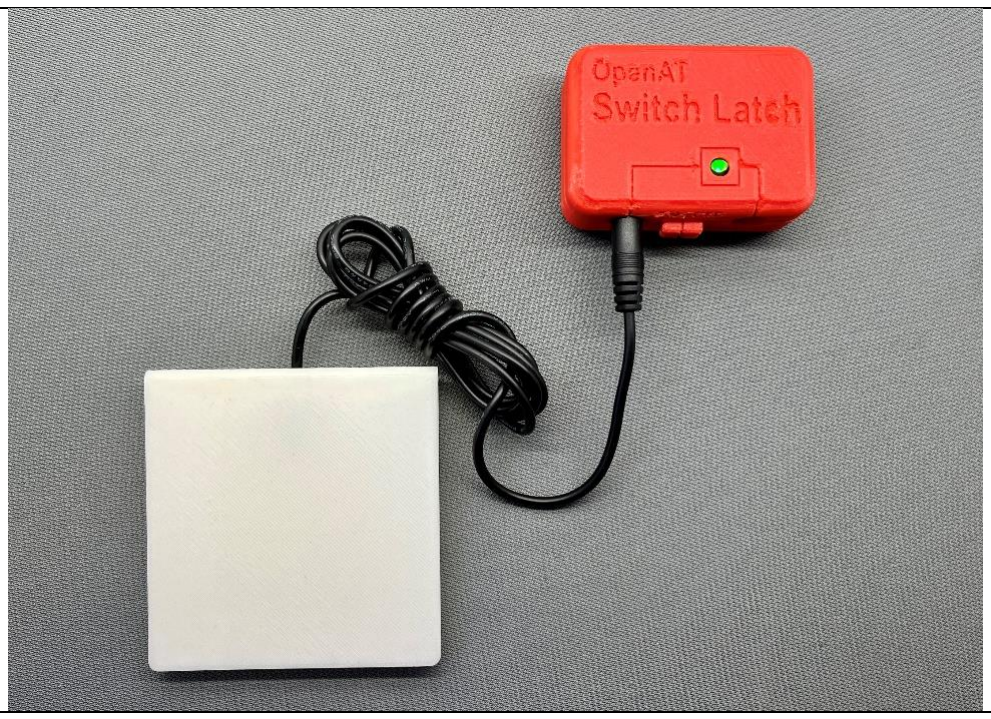
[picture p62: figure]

Files available at https://makersmakingchange.com/project/OpenAT-Switch-Latch/ | Page 20 of 22

### Testing

### Final Test

1. Attach an assistive switch to the input jack and an output device to the output jack.
2. Slide the power switch on.
3. Activate the switch. The LED should turn on and remain on and the output device should also activate.
4. Activate the switch again. The LED should turn off and remain off and the output device should turn off.

## ASSEMBLY GUIDE

Files available at https://makersmakingchange.com/project/OpenAT-Switch-Latch/ | Page 21 of 22

### Troubleshooting

If the device does not behave as expected, work through the following troubleshooting steps.

1. Ensure that the Power Switch is in the ‘On’ position.
2. Check that the battery is charged.
3. Check that the battery is properly inserted into the battery holder.
4. Inspect all solder joints. Ensure each joint has sufficient solder is not bridged to another joint.
5. Ensure the polarized components are installed in the correct orientation:
Component | Image | Note
Q1 – Mosfet IC | | The two leads that are connected together should be on the opposite side of the dot.
Q2 – Mosfet IC | | The two leads that are connected together should be on the opposite side of the dot.
U1 – Flip-flop IC | | The U-Shaped notch on the IC should be near the top, close to the “U1” label on the PCB.

## ASSEMBLY GUIDE

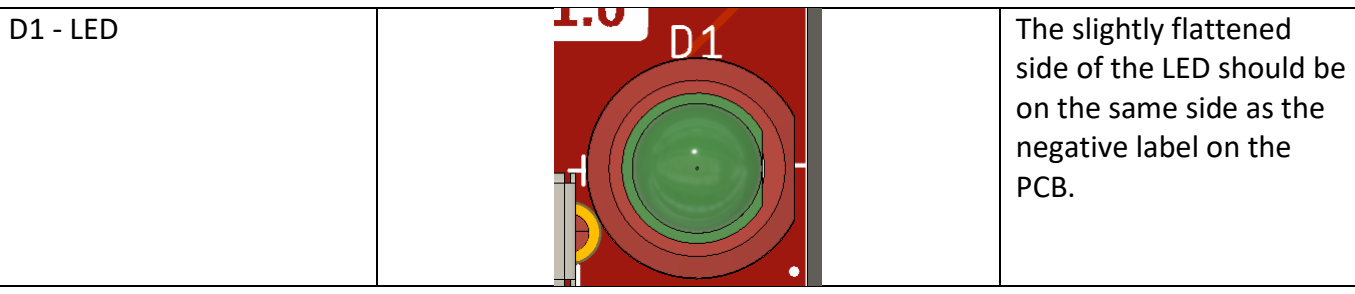
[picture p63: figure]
D1 - LED; The slightly flattened; side of the LED should be on the same side as the negative label on the PCB.

Files available at https://makersmakingchange.com/project/OpenAT-Switch-Latch/ | Page 22 of 22

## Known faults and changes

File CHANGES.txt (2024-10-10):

OpenAT Switch Latch Changelog

Version 1.1.2 | 2024-Oct-10
 - Added LED image to improve chance that LED is installed with correct polarity and with LED spacer
 - Re-arranged assembly steps so battery is installed into battery holder first to aid assembly
 - Added initial troubleshooting section to assembly guide.

Version 1.1 | 2023-Nov-23
	- Refactored Assembly Guide for better order (LEDs after shorter components)
	- Add 6th screw to BOM (1 for PCB, 4 for Enclosure, 1 for Battery Cover)

Version 1.01 | 2023-Nov-17
	- Enclosure_Top
		- Fixed ordering of On-Off
		- Added small chamfer to bosses and screw holes
	- Cleaned up repository

Version 1.0 | 2023-Feb-10
	- Initial release
		- CD74HC73E JK Flip Flop IC
		- 3D printed enclosure with Battery holder.
		- 3D Printed LED spacer added to simplify the assembly process
		- Added switch equipped jacks, allowing device to be turned on via plugging in.

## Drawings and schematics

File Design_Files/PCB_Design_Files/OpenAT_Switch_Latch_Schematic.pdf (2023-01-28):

### SJ-3566AN VCC

A

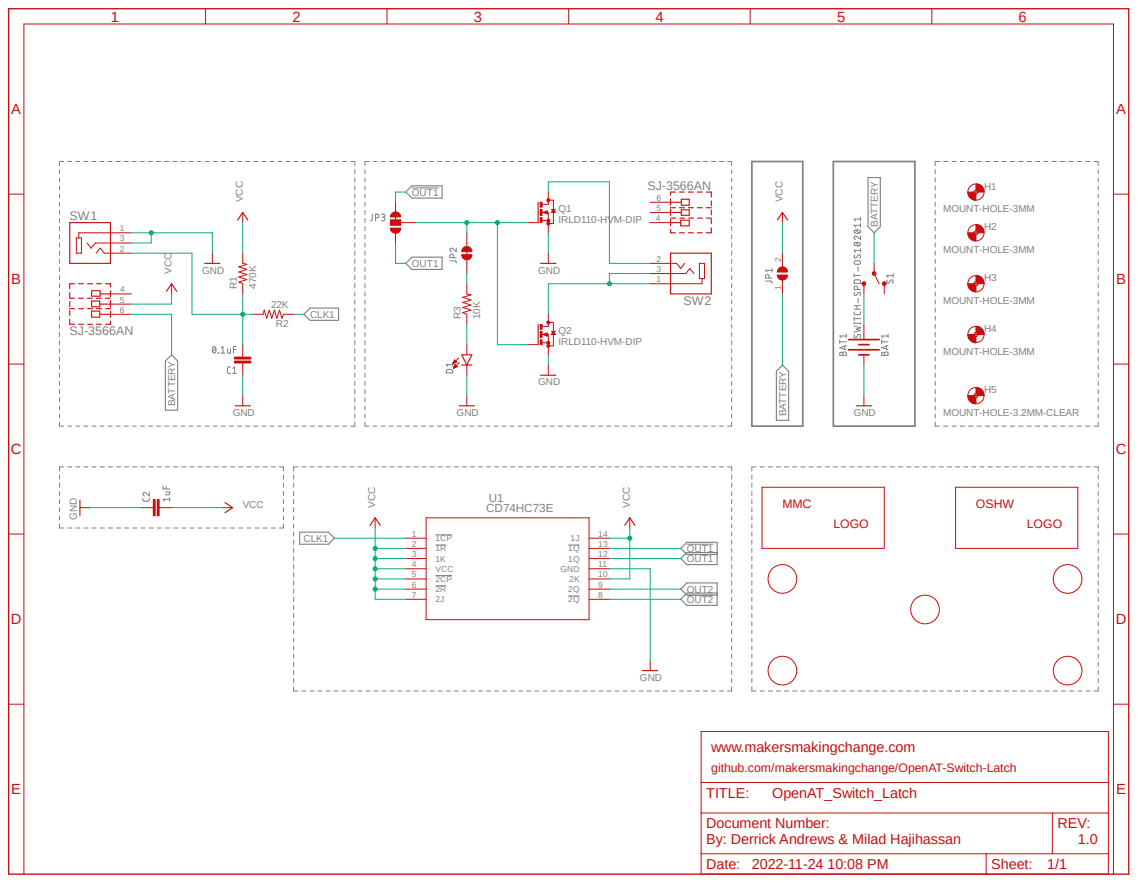
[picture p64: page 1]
GND; MOUNT-HOLE-3MM; 22K ⁴⁷⁰K; IRLD110-HVM-DIP; VCC GND; CD74HC73E VCC; GND VCC; MOUNT-HOLE-3.2MM-CLEAR VCC; VCC 4; 10 GND; H5 CLK1; CLK1; OUT2; OUT1; OUT1 BATTERY; BATTERY BATTERY; OpenAT_Switch_Latch; MMC; LOGO; OSHW

MOUNT-HOLE-3MM VCC

www.makersmakingchange.com
github.com/makersmakingchange/OpenAT-Switch-Latch
TITLE:

Document Number: By: Derrick Andrews & Milad Hajihassan | REV: 1.0

Date: 2022-11-24 10:08 PM | Sheet: 1/1

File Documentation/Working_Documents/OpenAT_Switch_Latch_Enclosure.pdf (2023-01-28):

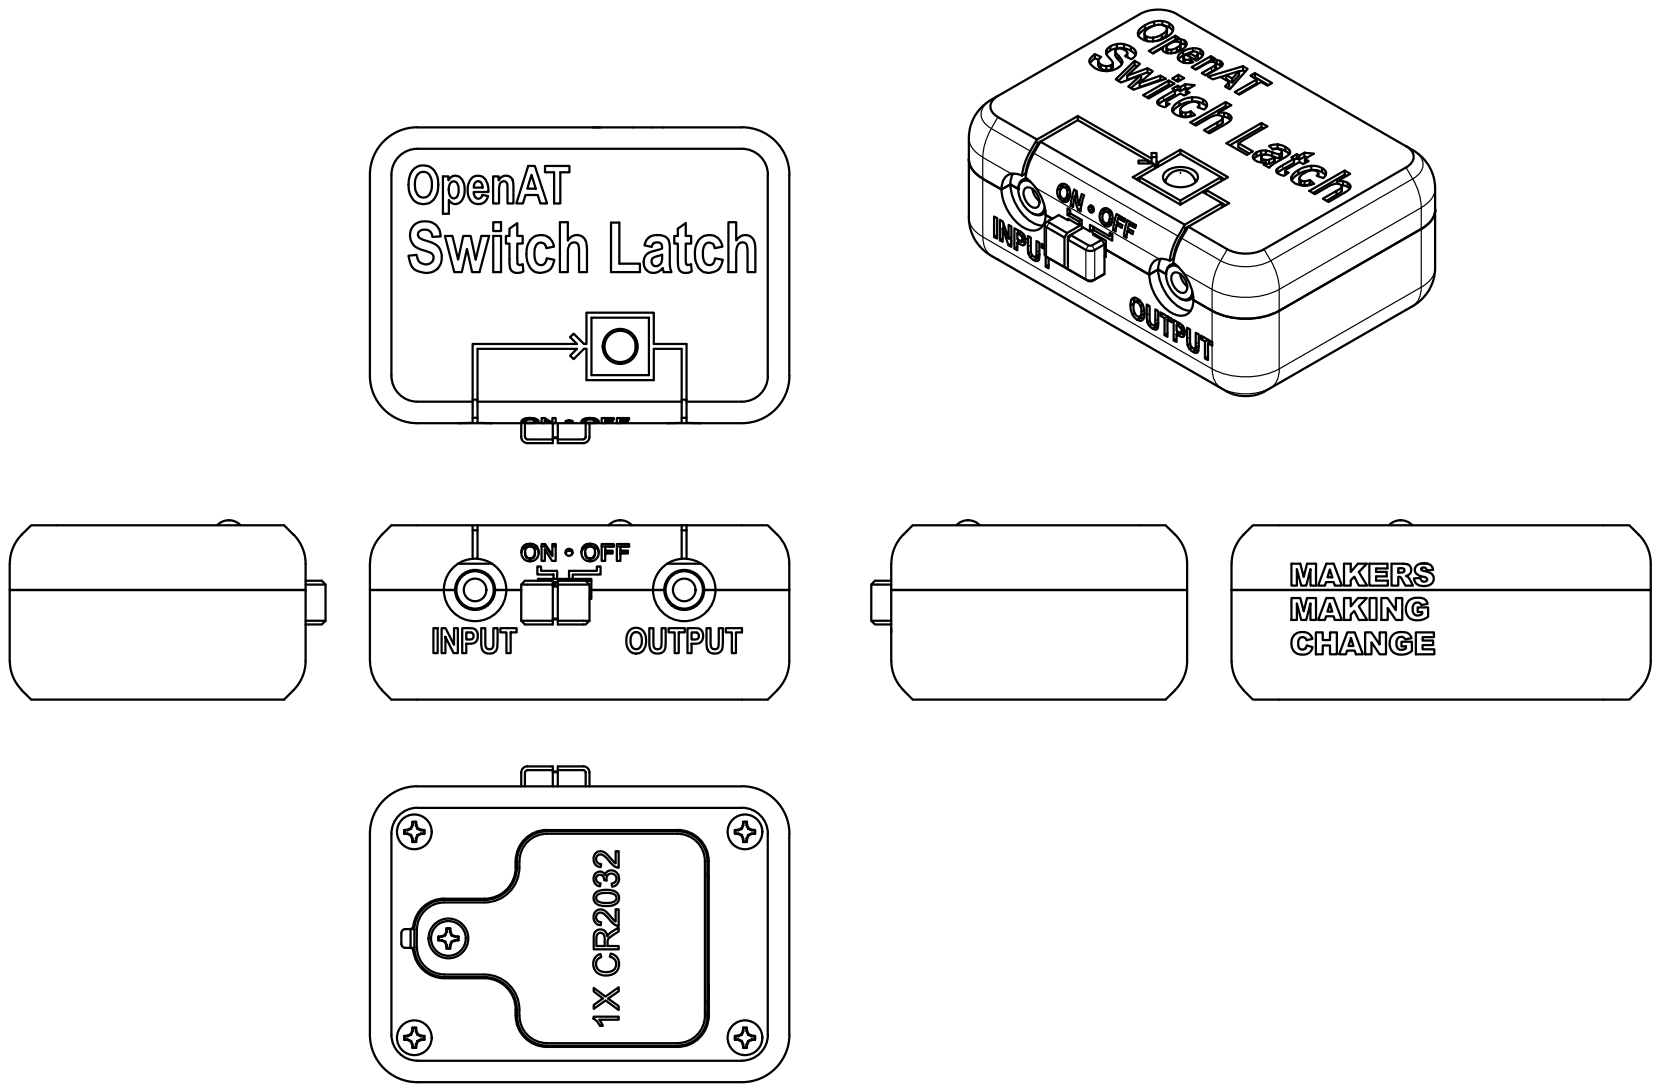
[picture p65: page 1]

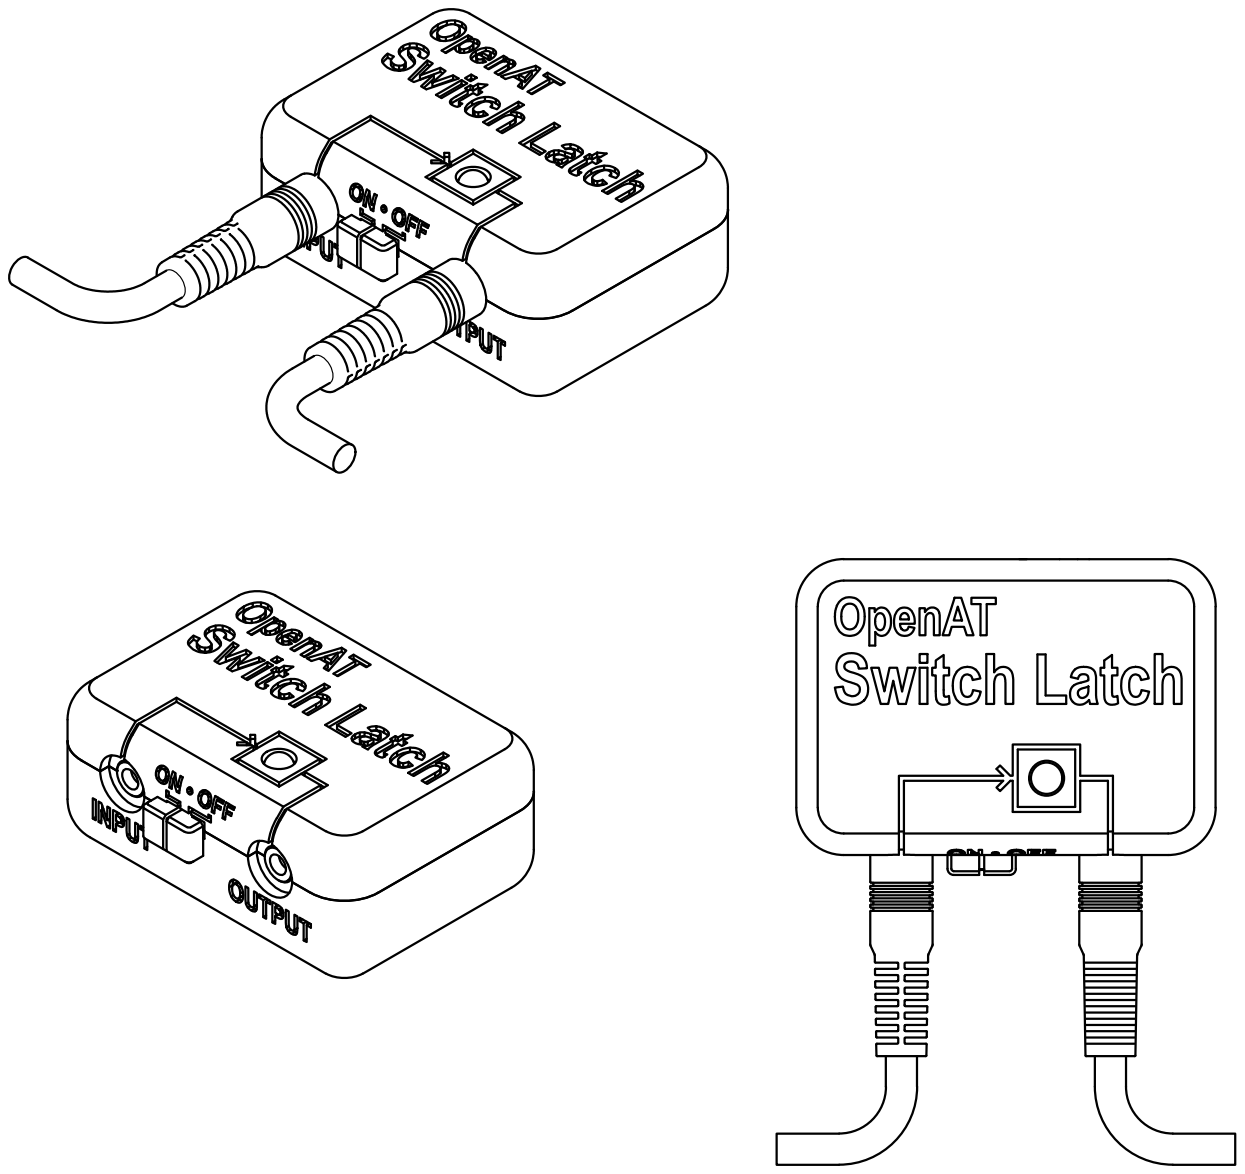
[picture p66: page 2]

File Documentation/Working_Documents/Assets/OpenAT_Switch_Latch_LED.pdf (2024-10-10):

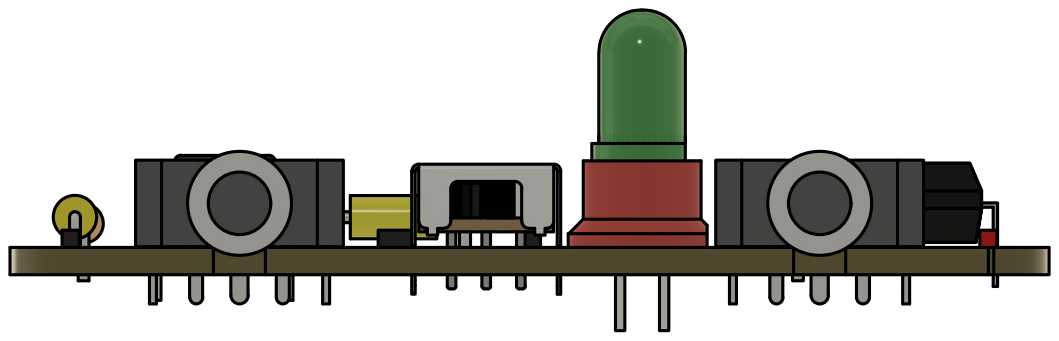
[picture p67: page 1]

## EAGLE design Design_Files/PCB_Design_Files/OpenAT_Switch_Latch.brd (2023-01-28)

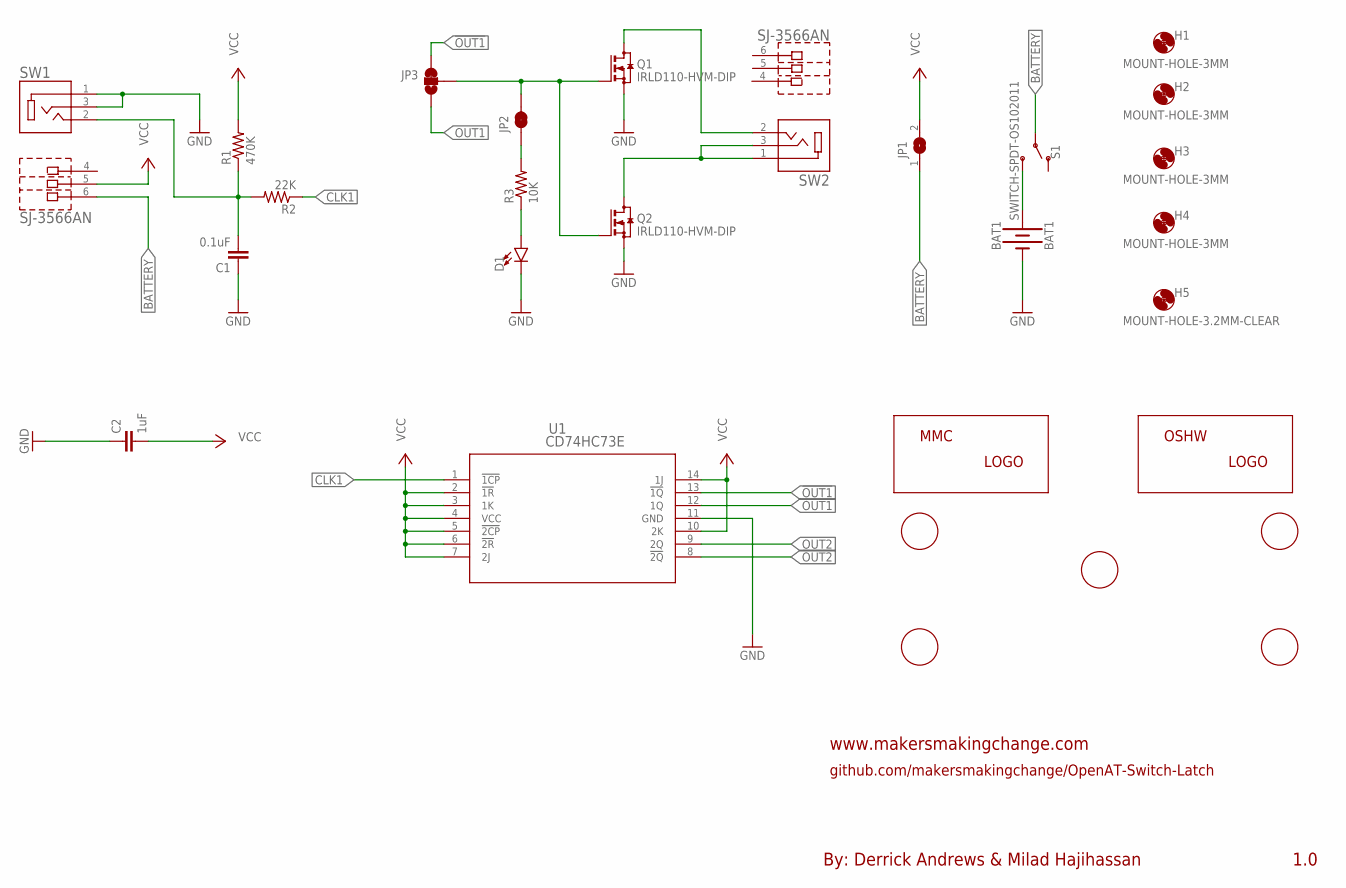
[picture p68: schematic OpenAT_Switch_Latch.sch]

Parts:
BAT1: BAT1; BATTCOM_20MM_PTH
C1: 0.1uF; CAP-050-030X075
C2: 1uF; CAP-050-030X075
D1: LED_5MM-5MM-GREEN; LED_5MM_GREEN
H1, H2, H3, H4: MOUNT-HOLE-3MM; HOLE-3MM
H5: MOUNT-HOLE-3.2MM-CLEAR; HOLE-3.2MM-CLEAR
JP1: SOLDERJUMPEROPENED; SOLDERJUMPER_OPENED_TRACE_SILK
JP2: JUMPERS-SMT_2_NC_TRACE_SILK; JUMPERS_SMT-JUMPER_2_NC_TRACE_SILK
JP3: JUMPERS-SMT_3_1-NC_TRACE_SILK; JUMPERS_SMT-JUMPER_3_1-NC_TRACE_SILK
LABEL_INPUT: MMC_LABEL-SW-INPUT; LABEL-INPUT
LABEL_LOGO: MMC_LOGO-SM; MMC_SMALL_LOGO
LABEL_OUTPUT: MMC_LABEL-SW-OUTPUT; LABEL-OUTPUT
Q1, Q2: IRLD110-HVM-DIP; HVM-DIP
R1: 470K; RESISTOR_0204/5
R2: 22K; RESISTOR_0204/5
R3: 10K; RESISTOR_0204/5
S1: SWITCH-SPDT-OS102011; SWITCH_SPDT_11MA1QS1
SW1, SW2: SJ-3566AN; CUI_SJ-3566AN
U1: CD74HC73E; 14-DIP
U$1: OSHW_LOGO-XSM; OSHW_X-SMALL_LOGO
U$2: MMC_LABEL-OPENAT; LABEL-OPENAT
U$3: MMC_LABEL-SWITCH-LATCH; LABEL-SWITCH-LATCH
U$4: MMC_LABEL-V1.0; LABEL-V1.0

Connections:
!OUT1: JP3.1, U1.13 (!1Q)
!OUT2: U1.8 (!2Q)
BATTERY: JP1.1, S1.2, SW1.6
CLK1: R2.1, U1.1 (!1CP)
GND: BAT1.-, C1.1, C2.1, D1.K (C), Q1.2 (S), Q2.2 (S), SW1.1, SW1.3, U1.11 (GND)
unnamed: BAT1.+, S1.3 (S)
unnamed: JP2.1, R3.2
unnamed: D1.A, R3.1
unnamed: Q2.3 (D), SW2.1, SW2.3
unnamed: Q1.3 (D), SW2.2
unnamed: C1.2, R1.1, R2.2, SW1.2
OUT1: JP3.3, U1.12 (1Q)
OUT1-SELECT: JP2.2, JP3.2, Q1.1 (G), Q2.1 (G)
OUT2: U1.9 (2Q)
VCC: C2.2, JP1.2, R1.2, SW1.5, U1.2 (!1R), U1.3 (1K), U1.4 (VCC), U1.5 (!2CP), U1.6 (!2R), U1.7 (2J), U1.10 (2K), U1.14 (1J)

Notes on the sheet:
www.makersmakingchange.com
1.0
By: Derrick Andrews & Milad Hajihassan
github.com/makersmakingchange/OpenAT-Switch-Latch

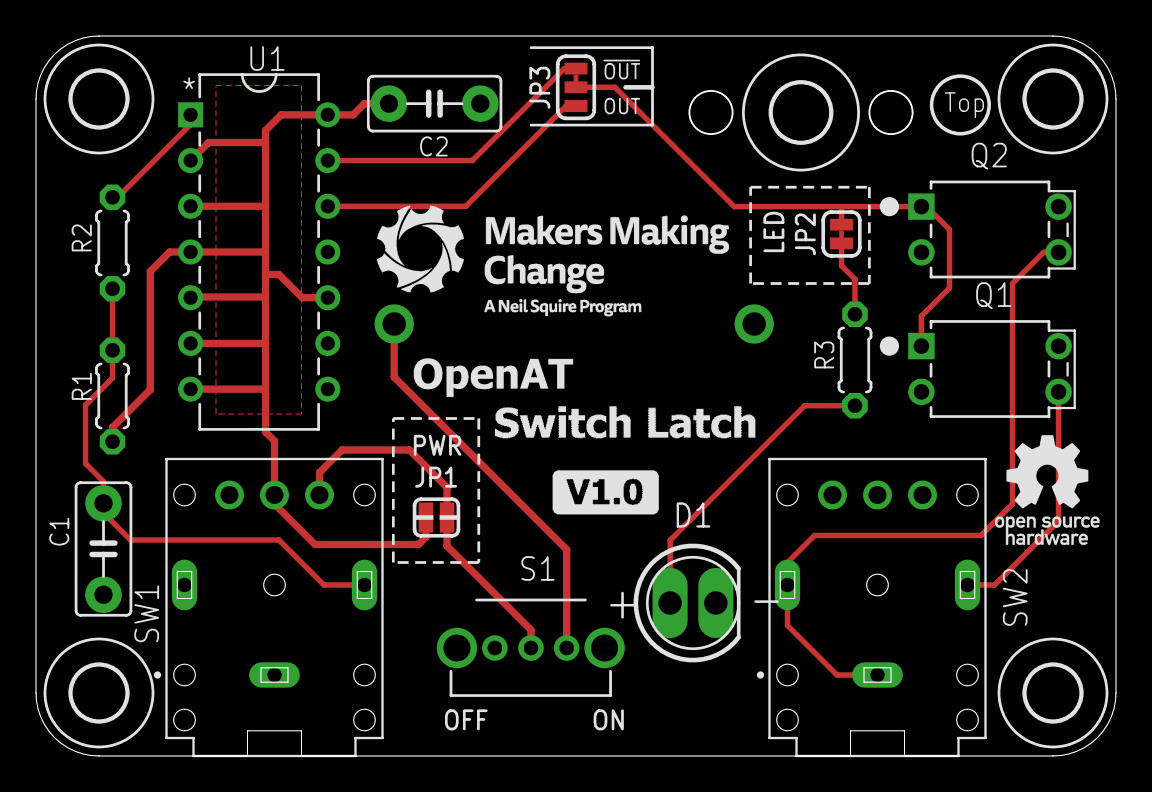
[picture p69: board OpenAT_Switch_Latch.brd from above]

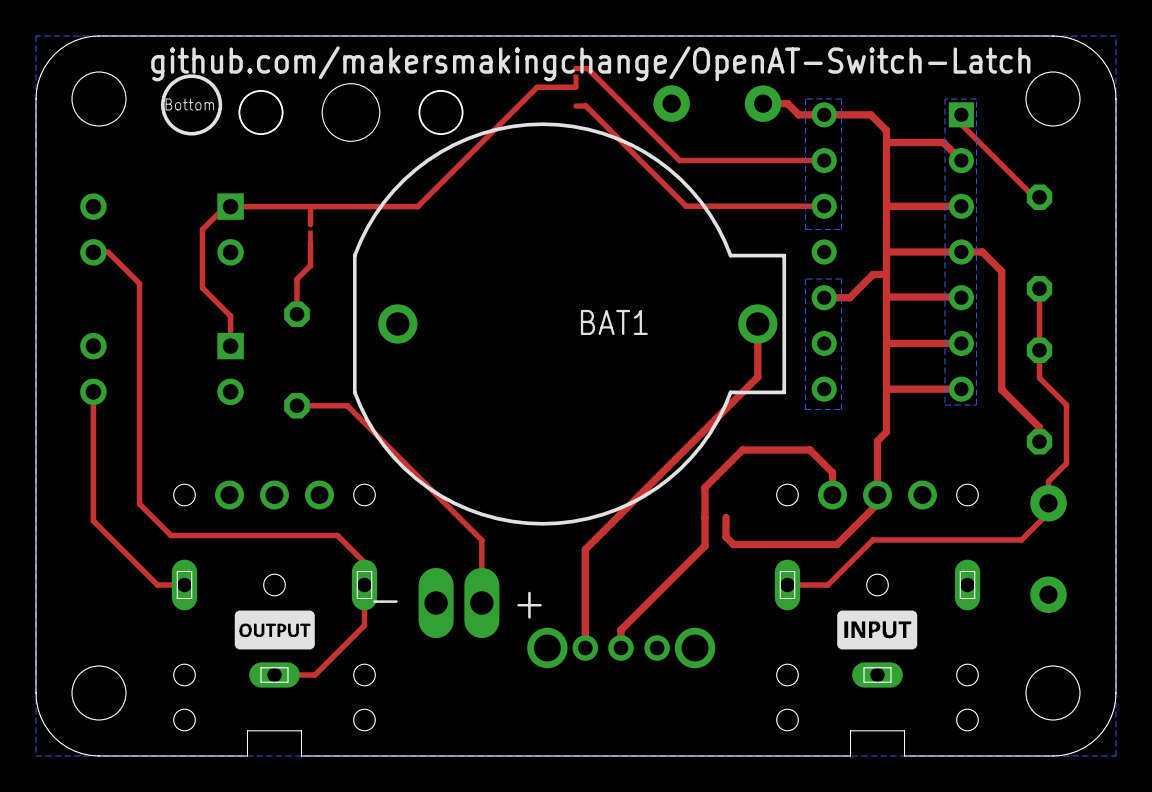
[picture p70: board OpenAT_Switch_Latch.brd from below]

Board: 2 copper layers, 60.0 x 40.0 mm, 28 parts (3 on the bottom side), 13 nets.

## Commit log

2023-01-28 OpenAT-Switch-Latch Version 1.0
    [Battery_Cover.stl, Enclosure_Bottom.stl, Enclosure_Top.stl, LED_Spacer.stl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]
2023-02-22 Updated BOM file links
    [OpenAT_Switch_Latch_BOM_v1.0.xlsx]
2023-02-28 Updated BOM file
    [OpenAT_Switch_Latch_BOM_v1.0.xlsx]
2023-11-18 Update 3D printing files to 1.01
    [Enclosure_Bottom.stl, Enclosure_Top.stl, OpenAT-Switch-Latch_Set.stl, OpenAT_Switch_Latch_v27.3mf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]
2023-11-18 Clean up documentation naming
    [OpenAT_Switch_Latch_BOM.csv, OpenAT_Switch_Latch_BOM.xlsx, OpenAT_Switch_Latch_BOM_v1.0.xlsx]
2023-11-18 Standardize folder naming
    [OpenAT_Switch_Latch.brd, OpenAT_Switch_Latch.sch]
2023-11-18 Update instructions
    - reordered steps to put LED insertion after other shorter components
    - fixed typos and incorrect photos
    - removed baked-in step numbers from photos
    - added alt text to all images
    - added battery to components list
    - added assistive switch and tape to tool list
    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
2023-11-23 6th screw
    Update Assembly Guide to v1.1
    Update BOM to 1.02 (add 6th screw)
    [OpenAT_Switch_Latch_BOM.xlsx]
2023-11-23 Update assembly guide to V1.2
    - Replaced visual BOM with table.
    - Updated component numbers to match build order
    - captured and added photos of battery and screws
    [OpenAT_Switch_Latch_BOM.csv, OpenAT_Switch_Latch_BOM.xlsx]
2024-08-26 Fix assembly guide typos
    Mosfet Q1 & Q2: shows qty = 1 instead of 2
    Flip-Flop IC: no number for Qty
    Green LED: shows qty = 3 instead of 1
2024-08-26 Update BOM to V1.2.1
    [OpenAT_Switch_Latch_BOM.csv, OpenAT_Switch_Latch_BOM.xlsx]
2024-10-10 Capacitor 3D Model Change
    Update capacitor package in PCB with smaller package
2024-10-10 Create graphic to aid LED placement
    Create Fusion drawing and Inkscape illustration to aid LED installation
2024-10-10 Update Assembly Guide
    Updated assembly guide:
    1. Added LED installation graphic and additional warning.
    2. Re-arranged steps to install battery in holder before soldering to hold assembly together.
    3. Added troubleshooting steps.

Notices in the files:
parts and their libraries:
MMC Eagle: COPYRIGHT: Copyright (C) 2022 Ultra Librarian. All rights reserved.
